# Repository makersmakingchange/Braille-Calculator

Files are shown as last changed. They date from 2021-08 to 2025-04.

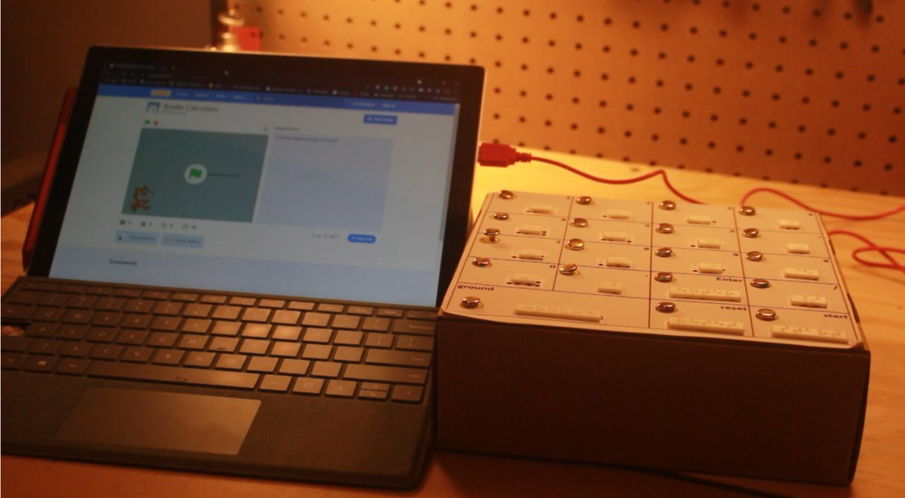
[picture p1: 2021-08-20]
photos-videos/main pic.png

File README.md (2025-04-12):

# Braille Calculator
This device aims aid visually impaired individuals to practice or preform mathematic operations by use of audible feedback and Braille labels.

# Documentation above includes: 
      - User Guide
      - 3D Print Guide
      - Assembly Guide
      - Bill of Materials
      - ChangeLog
      - Maker Checklist (use this if you are a maker to see the process of the build)
      - 3D Printed Braille Label STL's
      - Photos and a video of the device in use 

# Overview

The Braille Calculator uses a Makey Makey Classic, 3D printed Braille, and a scratch project to allow users to do simple addition, subtraction, multiplication, or division with audio feedback. The calculator allows the user to input a mathematical expression, guess the answer, and finally give the correct answer to compare with the user inputted answer and verify audibly if it was correct or incorrect. This device can be used with any PC, tablet, phone, or device with a USB (type-A) port, and internet connection.

# Usage

This device is intended for individuals that are visually impaired in an educational setting to practice math. The user is able to interact with an online calculator project created in Scratch that audibly interacts with their inputs using the brass contact points. The calculator includes 3D printed Braille labels of what each contact point represents. The calculator is capable of performing one multiplication, division, addition, or subtraction action at a time. This calculator is compatible with any device that has a USB (type-A) port and an internet connection.

An example of the usage of this device is in the downloadable section of this page.

# Build Instructions

SKILLS REQUIRED:

- 3D Printing
- Assembly

TOOLS:

- Glue (hot glue, stick glue, etc)
- 3D printer
- Scissors
- Ink Printer
- Wire stripper

# COMPONENTS

- (1x) Cardboard Box (8.5 x 11 x 3 inches)  Note: 3D print filament box works great
- (1x) Paper Printed with Braille Touchpad
- (19x) Alligator Clips (Note: The Makey Makey Classic this will come with 7 alligator clips) (https://www.amazon.ca/WGGE-WG-026-Pieces-Colors-Alligator/dp/B06XDM8BY1/ref=sr_1_20?dchild=1)
- (19x) 1-inch Brass Fasteners (https://www.amazon.ca/ACCO-Plated-Fastener-Fasteners-A7071710/dp/B004LWSFAK/ref=sr_1_1?dchild=1)
- (x19) 3D printed Braille Labels

# 3D PRINTING

Device requires 19 3D printed Braille labels. These are quick and take minimal filament. The 3D print files are downloadable on this page and do not require supports to print. The 3D printing guide file gives recommendations on settings for a successful print.

# Attribution

Through our partnership with Makey Makey, Katie Butzu, and Mark Lyons, workshops were hosted to help disability professionals learn how they could gamify their work. Then we challenged these disability professionals to create their own assistive technology for clients! This project was created by Tracy Zhang and modified by the MMC team to include 3D printed Braille.

<!-- ABOUT MMC START -->
## About Makers Making Change
[Makers Making Change Logo](https://www.makersmakingchange.com/)

Makers Making Change is a program of [Neil Squire](https://www.neilsquire.ca/), a Canadian non-profit that uses technology, knowledge, and passion to empower people with disabilities.

Makers Making Change leverages the capacity of community based Makers, Disability Professionals and Volunteers to develop and deliver affordable Open Source Assistive Technologies.

 - Website: [www.MakersMakingChange.com](https://www.makersmakingchange.com/)
 - GitHub: [makersmakingchange](https://github.com/makersmakingchange)
 - Bluesky: [@makersmakingchange.bsky.social](https://bsky.app/profile/makersmakingchange.bsky.social)
 - Instagram: [@makersmakingchange](https://www.instagram.com/makersmakingchange)
 - Facebook: [makersmakechange](https://www.facebook.com/makersmakechange)
 - LinkedIn: [Neil Squire Society](https://www.linkedin.com/company/neil-squire-society/)
 - Thingiverse: [makersmakingchange](https://www.thingiverse.com/makersmakingchange/about)
 - Printables: [MakersMakingChange](https://www.printables.com/@MakersMakingChange)

### Contact Us
For technical questions, to get involved, or to share your experience we encourage you to [visit our website](https://www.makersmakingchange.com/) or [contact us](https://www.makersmakingchange.com/s/contact).
<!-- ABOUT MMC END -->

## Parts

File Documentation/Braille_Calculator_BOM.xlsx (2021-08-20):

Device: Braille Calculator |  | Total Cost | Total Print time (hr) | Total filament (g)
Version: V1.0 | Date Created: 4/20/2021 | $78.39 | 2.33 | 18
Commercial Parts:
Part type (Electrical. Mechanical, Sanitization, ect) | Part Name | Quantity Needed | Pkg Quantity | Price per package | Price per Unit | Price for qty needed | Link
Housing | Cardboard Box (8.5 x 11 x 3 inches) Note: 3D print filament box works great | 1 | 1 | $0.00 | $0.00 | $0.00
Labeling | Paper Printed with Braille Touchpad | 1 | 1 | $0.00 | $0.00 | $0.00
Electrical | Makey Makey Classic | 1 | 1 | $63.23 | $63.23 | $63.23 | https://makeymakey.com/products/makey-makey-kit
Electrical | Alligator Clips (note if getting makey makey board starter setup this will come with 7 alligator clips) | 19 | 20 | 13.99 | $0.70 | $13.29 | https://www.amazon.ca/WGGE-WG-026-Pieces-Colors-Alligator/dp/B06XDM8BY1/ref=sr_1_20?dchild=1
Electrical | 1-Inch Brass Fastners | 19 | 100 | $7.49 | $0.07 | $1.42 | https://www.amazon.ca/ACCO-Plated-Fastener-Fasteners-A7071710/dp/B004LWSFAK/ref=sr_1_1?dchild=1
3D Printed Parts ESTIMATED PRICING USING 1KG ROLL COST: | $25.00
Part | Description | Quantity Needed | TOTAL Mass (g) | Estimated Price | Print Time (Min) | Link
Braille Tiles | 19 Braille Tiles that are used for lables | 20 | 18 | $0.45 | 140
 |  |  |  | $0.00
 |  |  |  | $0.00
 |  |  |  | $0.00
 |  |  |  | $0.00
 |  |  | Total Print Cost: | $0.45
Tools for Assembly
3D printer
glue
ink printer
scissors
wire stripper
Alternatives (if there are other sources for some parts link them below)
Part and description | Link

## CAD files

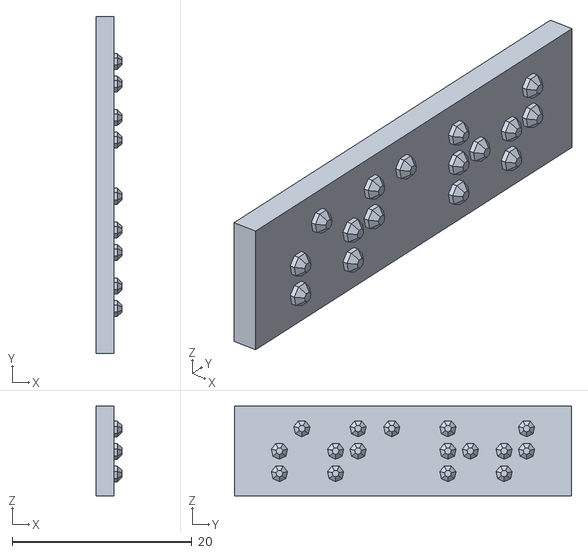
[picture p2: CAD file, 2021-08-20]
3D Print Files/calculator functions/nemeth_start.stl
2.92 x 37.5 x 10.0

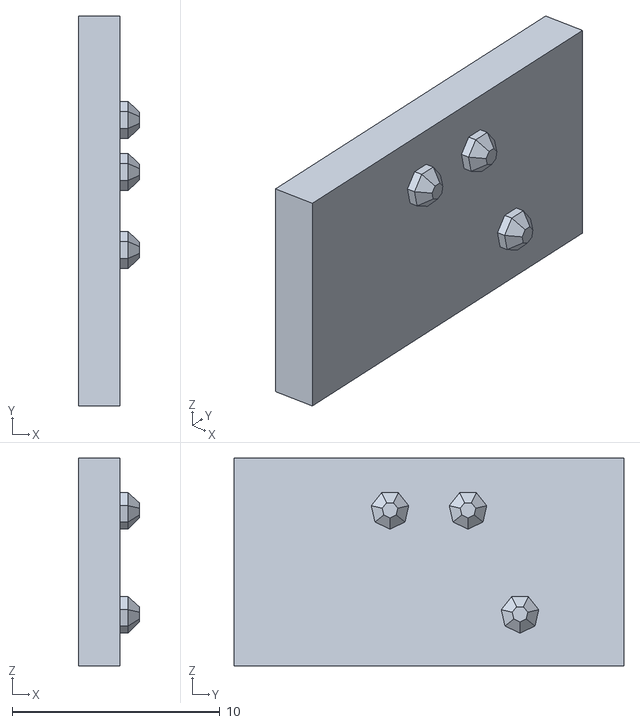
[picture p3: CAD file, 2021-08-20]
3D Print Files/math opperators/nemeth_multiplication_sign.stl
2.92 x 18.8 x 10.0

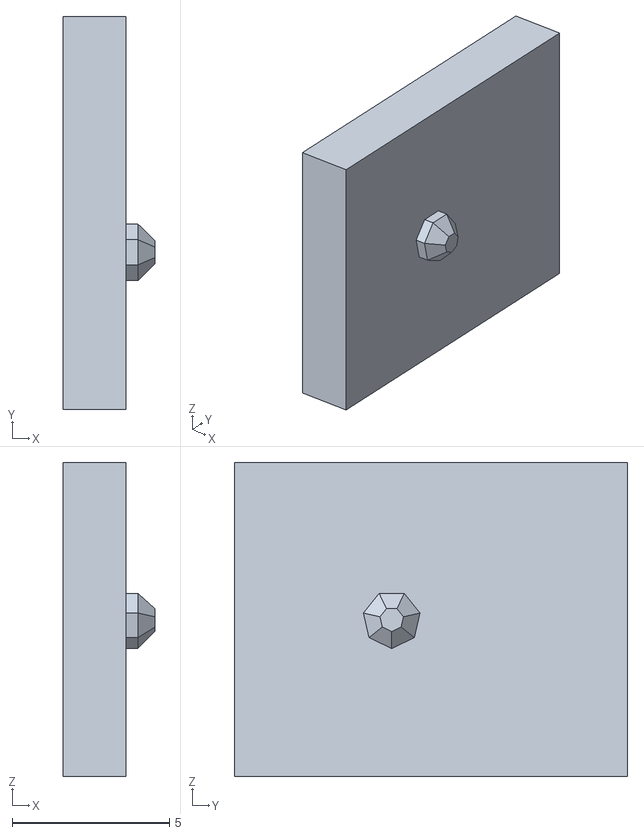
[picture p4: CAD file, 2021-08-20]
3D Print Files/numbers/nemeth_one.stl
2.92 x 12.5 x 10.0

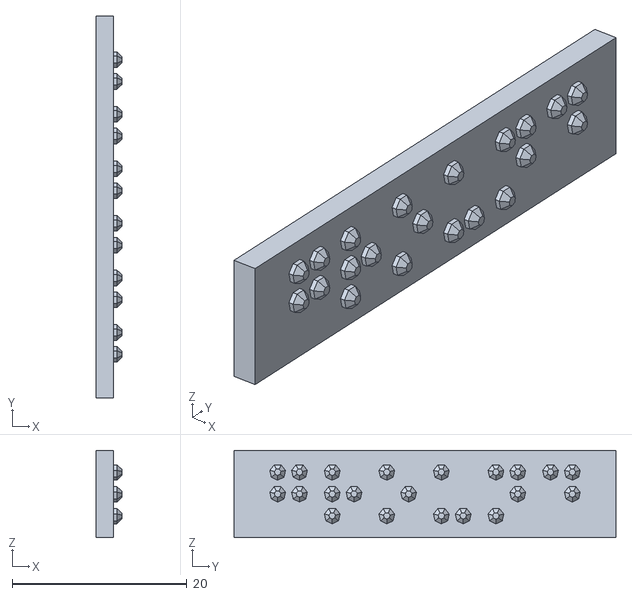
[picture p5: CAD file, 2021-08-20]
3D Print Files/calculator functions/nemeth_ground.stl
2.92 x 43.8 x 10.0

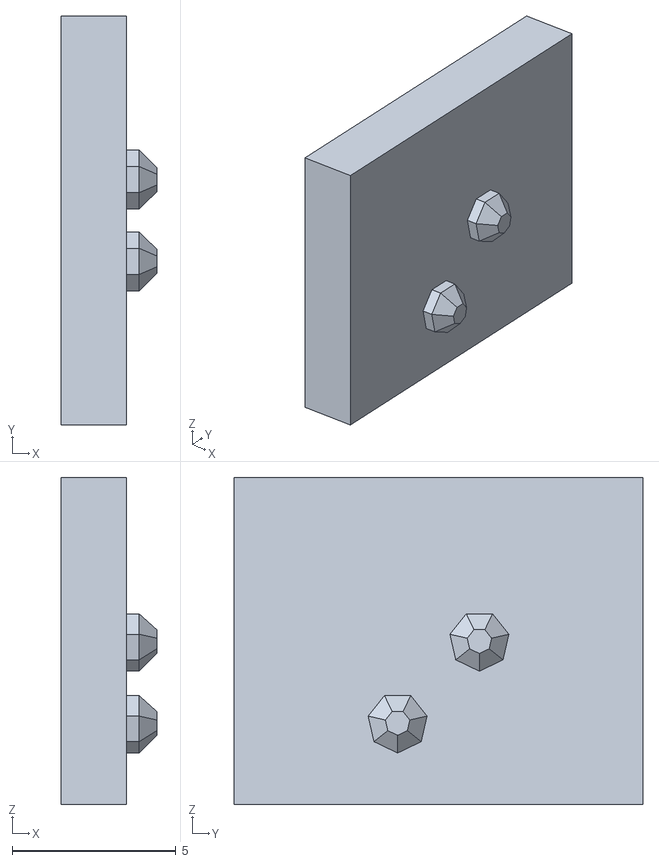
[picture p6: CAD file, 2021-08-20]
3D Print Files/numbers/nemeth_nine.stl
2.92 x 12.5 x 10.0

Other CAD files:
3D Print Files/math opperators/nemeth_divison_sign.stl
3D Print Files/calculator functions/nemeth_Enter.stl
3D Print Files/math opperators/nemeth_minus_sign.stl
3D Print Files/numbers/nemeth_three.stl
3D Print Files/calculator functions/nemeth_Reset.stl
3D Print Files/math opperators/nemeth_plus_sign.stl
3D Print Files/numbers/nemeth_seven.stl
3D Print Files/calculator functions/nemeth_decimal_point.stl
3D Print Files/numbers/nemeth_two.stl
3D Print Files/numbers/nemeth_six.stl
3D Print Files/numbers/nemeth_five.stl
3D Print Files/numbers/nemeth_eight.stl
3D Print Files/numbers/nemeth_zero.stl
3D Print Files/numbers/nemeth_four.stl

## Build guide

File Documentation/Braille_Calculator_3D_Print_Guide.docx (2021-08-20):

# 3D Printing Summary

Metrics | 3D Printed Braille
Total Print Time (min) | 140
Total Number of Components | 19
Typical Total Mass (g) | 18
Typical Number of Print Setups | 19

# 3D Printing Settings:

Important Notes:

- Ensure all Braille is printed vertically (shown in picture below)
- Print each label individually to eliminate stringing or blobbing in print

Print File Name | Qty | Total Print Time (hr:min) | Mass (g) | Infill (%) | Support (Y/N) | Layer Height/ Nozzle Diameter(mm) | Notes (orientation, special settings, etc)
Nemeth_zero.stl | 1 | 0:07 | .5 | 20 | N | 0.2/0.4 | Print in orientation given in STL.
Nemeth_one.stl | 1 | 0:07 | .5 | 20 | N | 0.2/0.4 | Print in orientation given in STL.
Nemeth_two.stl | 1 | 0:07 | .5 | 20 | N | 0.2/0.4 | Print in orientation given in STL.
Nemeth_three.stl | 1 | 0:07 | .5 | 20 | N | 0.2/0.4 | Print in orientation given in STL.
Nemeth_four.stl | 1 | 0:07 | .5 | 20 | N | 0.2/0.4 | Print in orientation given in STL.
Nemeth_five.stl | 1 | 0:07 | .5 | 20 | N | 0.2/0.4 | Print in orientation given in STL.
Nemeth_six.stl | 1 | 0:07 | .5 | 20 | N | 0.2/0.4 | Print in orientation given in STL.
Nemeth_seven.stl | 1 | 0:07 | .5 | 20 | N | 0.2/0.4 | Print in orientation given in STL.
Nemeth_eight.stl | 1 | 0:07 | .5 | 20 | N | 0.2/0.4 | Print in orientation given in STL.
Nemeth_nine.stl | 1 | 0:07 | .5 | 20 | N | 0.2/0.4 | Print in orientation given in STL.
Nemeth_division_sign.stl | 1 | 0:07 | 1 | 20 | N | 0.2/0.4 | Print in orientation given in STL.
Nemeth_minus_sign.stl | 1 | 0:07 | 1 | 20 | N | 0.2/0.4 | Print in orientation given in STL.
Nemeth_multiplication_sign.stl | 1 | 0:07 | 1 | 20 | N | 0.2/0.4 | Print in orientation given in STL.
Nemeth_plus_sign.stl | 1 | 0:07 | 1 | 20 | N | 0.2/0.4 | Print in orientation given in STL.
Nemeth_decimal_point.stl | 1 | 0:07 | 1 | 20 | N | 0.2/0.4 | Print in orientation given in STL.
Nemeth_enter.stl | 1 | 0:07 | 1 | 20 | N | 0.2/0.4 | Print in orientation given in STL.
Nemeth_ground.stl | 1 | 0:07 | 1 | 20 | N | 0.2/0.4 | Print in orientation given in STL.
Nemeth_reset.stl | 1 | 0:07 | 1 | 20 | N | 0.2/0.4 | Print in orientation given in STL.
Nemeth_start.stl | 1 | 0:07 | 1 | 20 | N | 0.2/0.4 | Print in orientation given in STL.

# Post-Processing

- If you notice any blobs on the side of the Braille tiles try using a blade to clean up the prints. Braille is hyper specific so any bumps or abnormalities on the print that could affect readability should be removed.

# Customization Options

- Braille is standardized so any changes in the model could render the tiles unreadable. Therefore, do not:
  - Resize the Braille
  - Alter the model in the slicer
  - Change the Braille dot orientation in any way

# Examples of Quality Prints:

- Below are some photos of acceptable prints and one example of what issues can occur if you print all together

Good Example of Prints Using Above Settings:

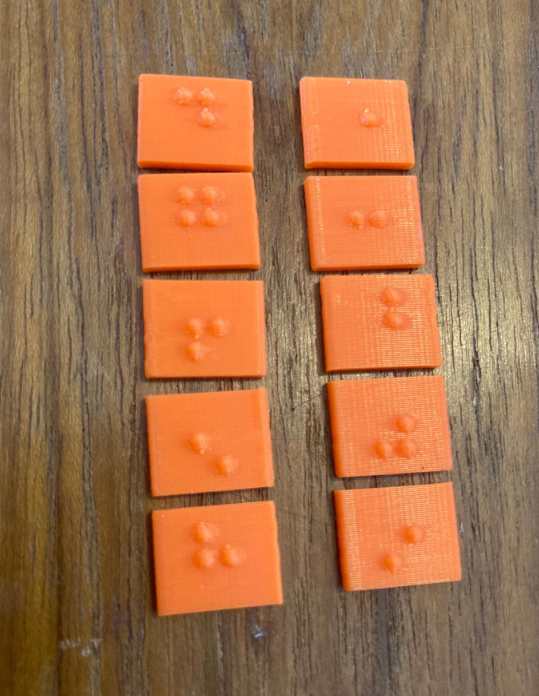
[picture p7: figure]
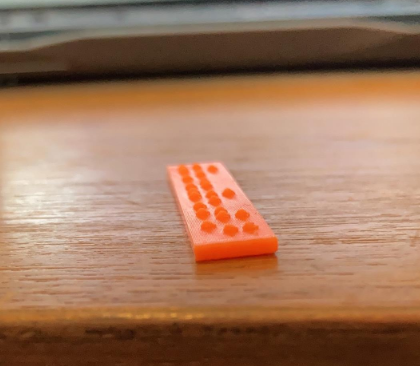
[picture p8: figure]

Below is how the Braille should be printed:

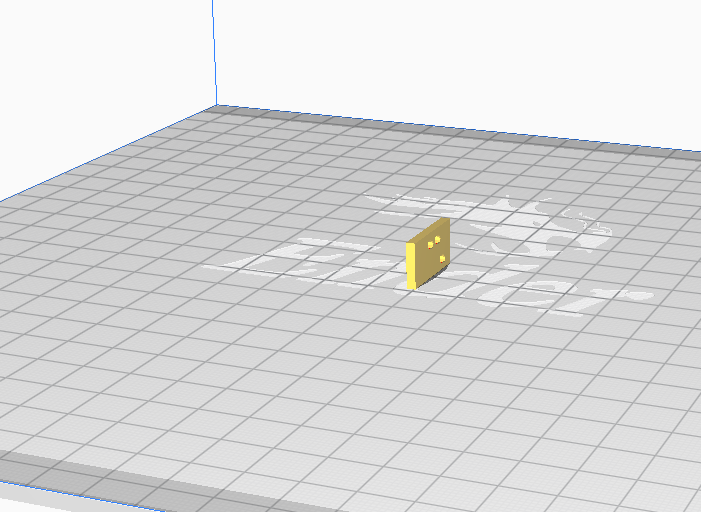
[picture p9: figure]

Example of Stringing When Printed in Groups Rather Than 1 by One:

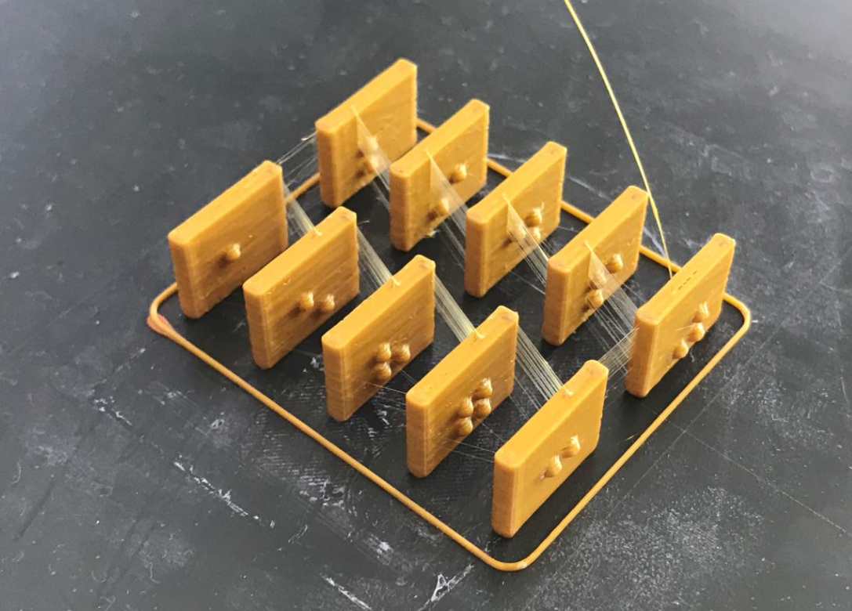
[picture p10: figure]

This can occur when printed in batches. May not occur on all printers and can be a relatively simple clean up. But to avoid this please print one Braille tile at a time

© 2021 by <Author>. This work is licensed under the CC BY SA 4.0 License: http://creativecommons.org/licenses/by-sa/4.0 Files available at <Replace with MMC Library Link> Page 4 of 4

V1.0. | <August> <2021> Braille Calculator 3D Printing Guide

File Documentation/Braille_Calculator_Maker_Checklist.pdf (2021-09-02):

V1.0 | <August> <2021>

## Braille Calculator

### MAKER CHECKLIST

© 2021 by <Author>.
This work is licensed under the CC BY SA 4.0 License: http://creativecommons.org/licenses/by-sa/4.0
Files available at <Replace with MMC Library Link> | Page 1 of 1

## Maker To Do List

- Discuss any customization or special tweaks the user may need for the device. Ensure the best to your ability that the user knows what the device is for/how it will work.
- Discuss with user the cost of materials (including possible shipping) of the components and agree on reimbursement
- Print the Braille and collect materials
- Follow assembly guide to build the device
- Contact user to let them know it is complete (update MMC forum request page if the request was through there)

## Items to Give to User

- Send the User Guide (and potentially video of how the device is used) in whatever method the user prefers (PDF, paper copy, ect)
- Device itself

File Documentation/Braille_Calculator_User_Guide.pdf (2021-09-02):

V1.0 | <August> <2021>

## Braille Calculator

### USER QUICK GUIDE

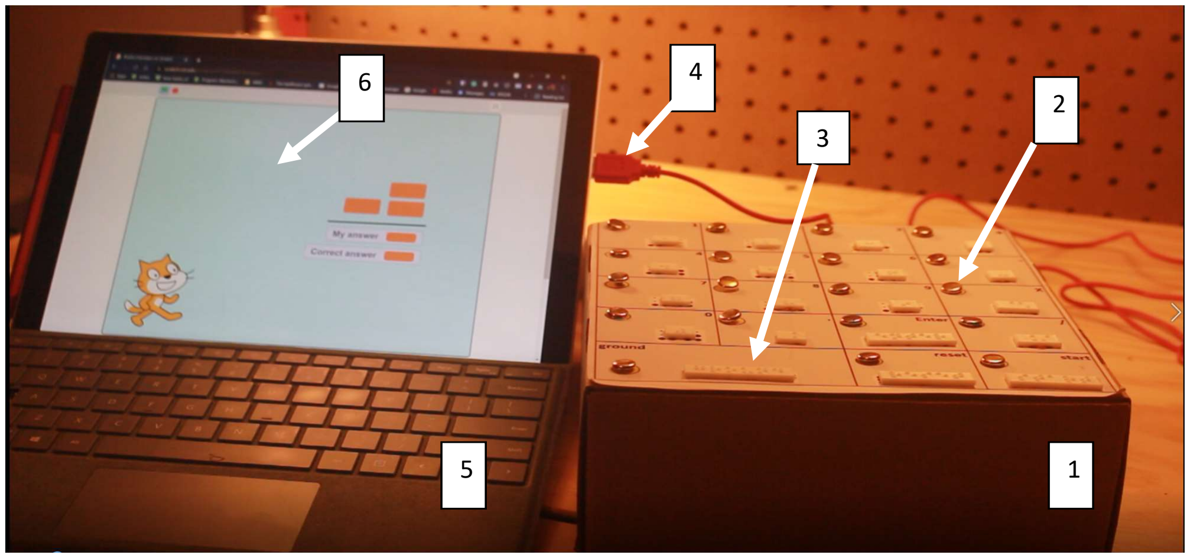
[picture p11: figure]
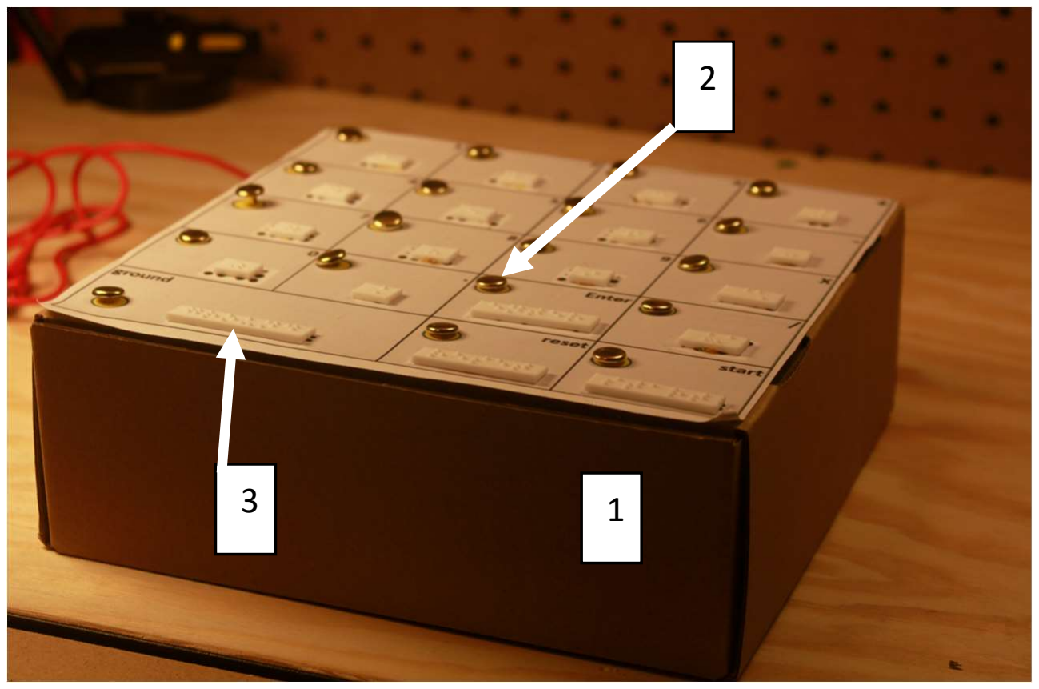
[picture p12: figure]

© 2021 by <Author>. This work is licensed under the CC BY SA 4.0 License: http://creativecommons.org/licenses/by-sa/4.0
Files available at <Replace with MMC Library Link> | Page 1 of 3

### Introduction

This device uses a Makey Makey Classic, 3D printed Braille, and a scratch project to create a calculator that allows users to do simple addition, subtraction, multiplication, or division with audio feedback. The calculator allows the user to input a mathematical expression, guess the answer, and finally give the correct answer to compare with the user inputted answer and verify audibly if it was correct or incorrect.

### Features

The Braille calculator devices features:

### USER QUICK GUIDE

Files available at <Replace with MMC Library Link> | Page 2 of 3
1. Closed cardboard box containing electronics (Makey Makey) inside and Braille labels and Brass fasteners attached on face of box.

### 2. Brass fasteners contact points that are used to input the values

3. 3D printed Braille labels that indicate what each brass fastener button corresponds to

### 4. USB cable coming from the Braille calculator 5. Electronic device with a USB port and internet connection 6. Browser open with the calculator program webpage opened. This can be found here:

https://scratch.mit.edu/projects/471598668

### Usage

Use a keyboard to test the calculator:

- Press “Spacebar” to start the calculator, then listen to the voice prompt
- Press “Enter” after each input of numbers, operations and answers
- To start over during calculation, click the mouse (again, the mouse cursor needs to be hovered over the project screen when clicked)

Braille Calculator Set-Up:

- To set up the device, ensure that the Calculator’s USB is plugged into the device and the calculator webpage is open on the desired device
- Examine the Braille calculator. The brass fasteners will be used as “buttons” for input to the calculator program. Each brass fastener corresponds to the 3D printed Braille label on its right.
- This device relies on using two points of conductive contact from the same source, to complete the circuit. Some common examples would be your hands, antistatic wrist wrap, or any conductive household items, such as cutlery, to complete the circuit of the Makey Makey device.
- During the operation, the brass fastener for “ground,” which can be found on the bottom left, needs to be in contact the entire time, while your second contact touches the desired input’s brass fastener.
Note: An example would be your left index finger holding the “ground” brass fastener, while your right index finger touches the “one” brass fastener. As the circuit is completed, the calculator will then register the input, and your right index finger can be released.

Steps using Makey Makey Braille calculator:

- To start the calculator, hold the brass fastener “ground,” press the brass fastener “start,” then listen to the voice prompt “What’s the number?”

### USER QUICK GUIDE

Files available at <Replace with MMC Library Link> | Page 3 of 3
- To input desired number, hold the brass fastener “ground,” press the brass fastener of the desired number, then press the brass fastener “enter.” This will trigger the voice prompt “What’s the operation?”
- To input desired operation and number, continue in same manner as above while listening to the voice prompts.
- When the calculation is done, the voice prompts will confirm if your answer is correct or not. This means the calculation has been completed.
- When finished, or if wanting to start over during calculation, hold the brass fastener “ground” and press the brass fastener “reset.”

### Compatibility

- Any device with an internet connection and USB type A connection. This includes laptops, PC, tablets, phones with USB adapter.

### Specifications

- Size: This depends on the box used but the minimum size must be (8.5 x 11 x 3 inches)
- Weight: approximately 1lb

### Cleaning

- The cardboard can be wiped down using sanitizing wipes but anything that uses liquid will ruin the paper and cardboard box quality.
- 3D printed Braille should not be cleaned with high heat but can be wiped/cleansed with sprays

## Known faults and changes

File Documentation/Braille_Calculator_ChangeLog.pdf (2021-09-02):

V1.0 | <August> <2021>

## Braille Calculator

### CHANGELOG

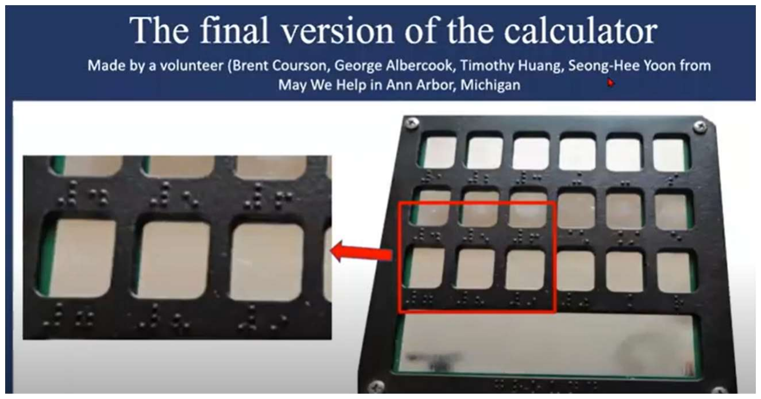
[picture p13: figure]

© 2021 by <Author>. This work is licensed under the CC BY SA 4.0 License: http://creativecommons.org/licenses/by-sa/4.0
Files available at <Replace with MMC Library Link> | Page 1 of 1

Forum link that follows development of this device: https://forum.makersmakingchange.com/t/tracyspecialist-makey-makey-for-blindness-autism/1361/29

## Version 0.0 | Date: 2020

- This design was originally prototyped by Tracy Zhang and their team. The teams final version can be seen here: https://makeymakey.com/blogs/how-to-instructions/makey-makey-braillecalculator-by-tracy-zhang
- Overall goal was to create a calculator for individuals who are living with vision differences using the Makey Makey device

## Version 0.5| Date: 2020

- Brent Courson developed the below version as a continuation of this device. Little details are known on this design but they shared a video of the device in action here: https://drive.google.com/file/d/1z8vUMuvy9QH_68tkiRzJQSt9UqOVPhYk/view

## Version 1.0| Date: 2021

- This version was developed by Tyler Fentie as an intern at Makers Making Change. It worked off of Version 0.0 and added Braille and more documentation for the makers and the users.
- All of the Makey Makey and Scratch components were kept exactly the same but due to lack of availability to braille labels used in the original version 3D printed Braille Tiles were developed.
